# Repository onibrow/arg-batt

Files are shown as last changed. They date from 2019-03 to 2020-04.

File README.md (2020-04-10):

# Arias Research Group - Battery Testing Board

### Seiya Ono Sp'19

## Overview

The board was designed such that the Photon could both drive and discharge the battery cell attached. The battery load resistor was chosen to be 0805 SMD so it could potentially be upgraded to handle higher discharges. Other than that, there are redundant connectors coming off so the user can access needed pins in different ways. The board also features two exposed test pads to probe the resistance of the load resistor precisely, given the user measures it before soldering on the Photon.

The pins below the Photon as well as the battery connection pins are meant for test points. The slide switch can disconnect the battery from the circuit as to not discharge when unnecessary. There are 5 indicator LEDs on the side that can be programmed by the user.

The BOM can be found as `bom.csv` and includes the parts used to populate the board.

### Resistor Selection

The [10 Ohm Resistor](https://www.digikey.com/product-detail/en/stackpole-electronics-inc/RNCF0805AKT10R0/RNCF0805AKT10R0CT-ND/4250701) was chosen by searching through Digikey with [these filters](https://www.digikey.com/products/en/resistors/chip-resistor-surface-mount/52?k=&pkeyword=&sv=0&pv7=2&pv1989=0&pv3=651&pv3=667&pv3=696&pv16=39329&pv1127=i2&sf=1&FV=-8%7C52&quantity=&ColumnSort=0&page=1&stock=1&nstock=1&photo=1&pageSize=50) enabled.

If that link somehow is broken, the filters are as follows:

`Product Index > Resistors > Chip Resistor > Surface Mount`

Part Status: Active

Package / Case: 0805

Packaging: Cut Tape

Tolerance: 0.01%, 0.02%, 0.05%

Number of Terminations: 2

In stock: Checked

Normally Stocking: Checked

Photo: Checked

## Tips

When soldering, start with the smallest components, as they are the hardest to solder. Then move to the test points and slide switch, then the Photon. When soldering the Photon, make sure it is aligned well so that all the pads have enough room to contact the castelated board.

## Specifications

From Dr. Evans:

Idea is to carry out multi-cycle testing of a Panasonic coin cell (about 3 million cycles). With the present arrangement (a Photon mounted on a breadboard) we have reached ~ 2 million cycles and still going. The design connects the DAC output of the Photon (nominally 0 – 3.3V DC) to the positive terminal of the cell holder via a 10 Ohm resistor. The negative terminal of the cell holder is connected to GND on the Photon. Wires run from either side of the resistor to the analog input connections on the Photon so that the current can be determined from the voltage drop across the resistor (A3 to A5) and the cell voltage determined by one of the connections (A3). We have software that brings the DAC output to greater than the cell voltage during charge and lowers it to below cell voltage during discharge. A cycle takes approximately 400 ms and the data are relayed via Webhook to ThingSpeak (Math Works’ version of the cloud) for plotting/analysis.

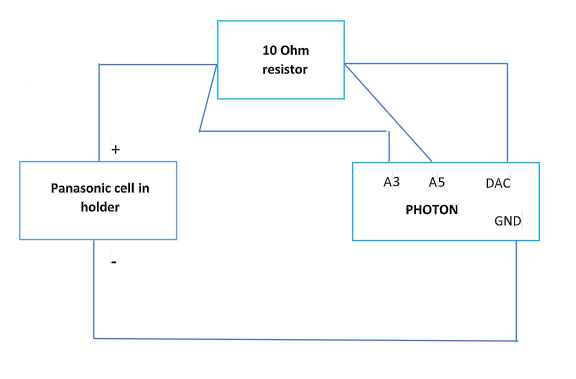
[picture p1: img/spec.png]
spec


### Task

1. Build present design but with soldered connections. Two Photons without header pins should be here by next week. We have cell holders and cells.
1. Set up the Photons and load code (I will supply).
1. Run a couple of cells to 3 million cycles or failure, collecting data.
1. See what we can do next.

Useful Links:

[Photon](https://store.particle.io/products/photon)

## Possibilities

* External power - through maybe a barrel jack to provide external power to the entire board, so that the photon's uUSB isn't stressed
* Push buttons for Photon configuration - allows external user to set up and start different testing procedures
* Accurate ammeter for measuring current.
* Instead of having a soldered on resistor, can use [SIP Sockets](https://www.digikey.com/product-detail/en/mill-max-manufacturing-corp/346-43-102-41-013000/ED6464-02-ND/1212288) to make impermanent connections with precision through hole resistors. This way, they can be swapped in and out for future proofing.

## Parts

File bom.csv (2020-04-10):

Digi-Key Part Number | Quantity | Description
RNCF0805AKT10R0CT-ND | 1 | RES 10 OHM 0.05% 1/8W 0805
1878-1001-ND | 1 | PHOTON WITHOUT HEADERS
311-330LRCT-ND | 5 | RES SMD 330 OHM 1% 1/16W 0402
846-1211-2-ND | 0 | LED GREEN-YELLOW CLEAR 1006 SMD
SML-D12U1WT86CT-ND | 1 | LED RED DIFFUSED 1608 SMD
511-1578-1-ND | 1 | LED GREEN DIFFUSED 0603 SMD
475-2486-1-ND | 1 | LED ORANGE DIFFUSED 0603 SMD
67-1550-1-ND | 1 | LED YELLOW DIFFUSED SMD
475-2816-1-ND | 1 | LED BLUE DIFFUSED 0603 SMD
36-5001-ND | 10 | PC TEST POINT MINIATURE BLACK
CKN5001-ND | 1 | SWITCH SLIDE SPDT 6A 120V

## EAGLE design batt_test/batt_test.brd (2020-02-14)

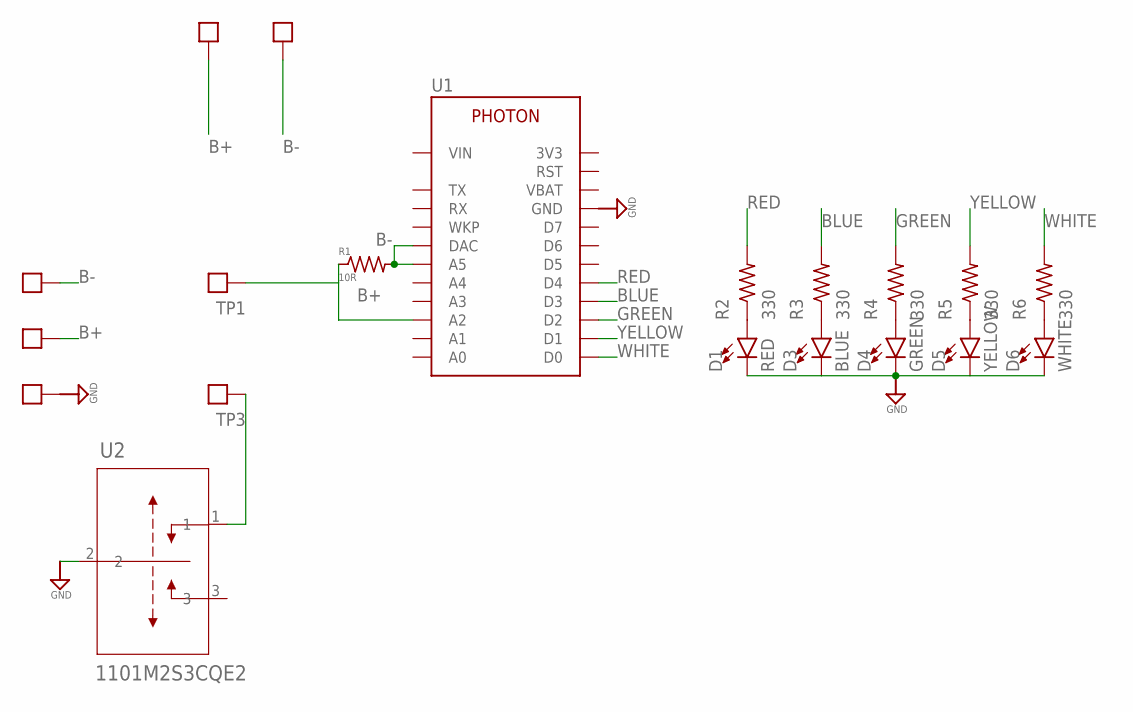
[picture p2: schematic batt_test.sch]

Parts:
B+: TEST_POINTTHRU; TEST_POINT
B-: TEST_POINT; TEST_POINT-1206
B-2: TEST_POINTTHRU; TEST_POINT
D1: RED; LED-0603
D3: BLUE; LED-0603
D4: GREEN; LED-0603
D5: YELLOW; LED-0603
D6: WHITE; LED-0603
POS: TEST_POINT; TEST_POINT-1206
R1: 10R; R0805
R2, R3, R4, R5, R6: 330; R0402
TP1, TP2, TP3: TEST_POINTTHRU; TEST_POINT
U1: PHOTON
U2: 1101M2S3CQE2

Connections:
B+: B+.1, POS.1, R1.1, TP1.1, U1.A2
B-: B-.1, B-2.1, R1.2, U1.A5, U1.DAC
BLUE: R3.2, U1.D3
GND: D1.C, D3.C, D4.C, D5.C, D6.C, TP2.1, U1.GND, U1.GND@1 (GND), U2.2
GREEN: R4.2, U1.D2
unnamed: TP3.1, U2.1
unnamed: D1.A, R2.1
unnamed: D3.A, R3.1
unnamed: D4.A, R4.1
unnamed: D5.A, R5.1
unnamed: D6.A, R6.1
RED: R2.2, U1.D4
WHITE: R6.2, U1.D0
YELLOW: R5.2, U1.D1

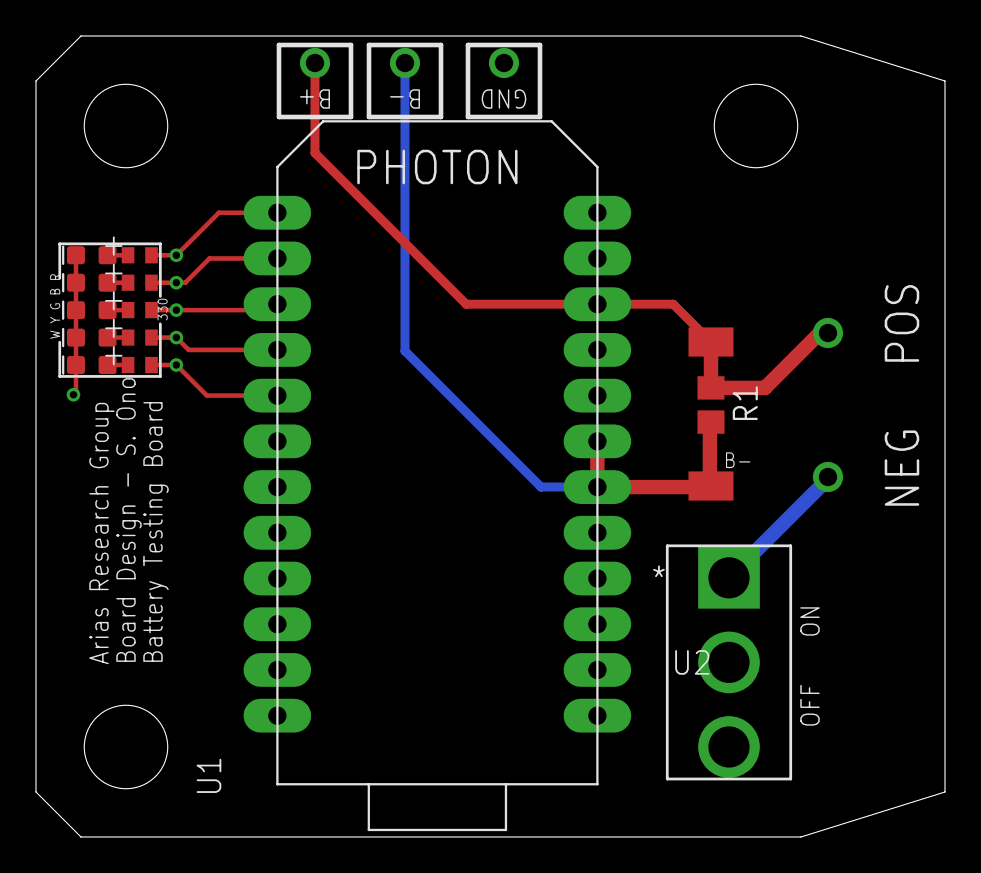
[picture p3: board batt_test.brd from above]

Board: 2 copper layers, 50.5 x 44.5 mm, 23 parts (0 on the bottom side), 14 nets.

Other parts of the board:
U$1, U$3, U$4: 4-40-HOLE

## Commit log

2019-03-17 start schematic
    [batt_test.sch]
2019-03-17 start board layout
    [batt_test.brd, batt_test.sch]
2019-03-18 add batt test point
    [batt_test.brd, batt_test.sch]
2019-03-18 finish first proto
    [batt_test.brd, batt_test.sch]
2019-03-19 add bom
    [Bom_7799568.csv]
2019-04-29 update bom and gerber
    [Bom.csv, Bom_7799568.csv, batt_test.brd, batt_test.sch]
2019-05-02 new contacts and bom
    [batt_test.brd, batt_test.sch]
2020-02-14 one last time?
    [Bom.csv, batt_test.brd, batt_test.sch]
2020-04-10 final revision push
    [Bom.csv, bom.csv]
